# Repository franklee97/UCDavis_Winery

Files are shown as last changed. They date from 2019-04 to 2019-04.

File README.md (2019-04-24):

# UCDavis_Winery

This repo contains all the information regarding my project at UC Davis RMI Winery. The goal of the project was to come up with a system that can collect and record data from a fermentation tank inside the winery. The data that were collected were Brix, or sugar concentration of a wine, Redox, and temperature. This system consisted of a PCB carrier board with mounting holes and necessary electrical connections, modules that either plugged into the mounting holes of the carrier board or resided on a din rail, and a box to hold all the components and wires. This repo has software information as well as hardware and layout information of the box. The system was only tested with one fermentation tank, but it is capable of expanding the number of tanks by a simple change in code. It also has the capability of sending data wirelessly via Bluetooth or XBee.

## BOM
This folder has the Bill of Materials(BOM) necessary for this project. The parts were ordered in four different batches. `Final.xlsx` contains all the components that are necessary for this project as some parts were never used from other orders.

## Code
This folder contains the code necessary to collect data. It contains two Arduino code, `data_collection_brix.ino` and `data_collection_redox.ino`. They both use `ModbusMaster.h` library to read values from the slave devices and store into SD cards, but the brix code reads two sensors' data while the redox code read one sensor's data. The polling rates for each code are also different. The code was written for Arduino Mega board, but any Arduino boards with at least two Serial ports will suffice. 

### Data Format
The data are stored as `.csv` file. The sample data for each code are inside each code folder. The name of the file uses the following format: `DATA[month][date].csv`. For example, if it is a data file from January 5th, the filename would be `DATA15.csv`. A new file was created every day to prevent an overload inside one file. More information about how this was done is in the comments for each code.

## Diagram
This folder contains two files, `Circuit_Diagram.png` and `Data_Flow_2.0.pdf`. `Circuit_Diagram.png` shows a circuit level diagram of how everything is being powered. It also shows data communication as well. `Data_Flow_2.0.pdf` is a diagram that specifically shows how data is being transferred between the modules inside the system. `Circuit_Diagram.png` was created using EAGLE and `Data_Flow_2.0.pdf` was created using Microsoft Vizio.

## Schematic
This folder contains a folder named `carrier_final` which has the necessary EAGLE files for the carrier PCB. It also has a top and bottom layout pictures given by Oshpark. The folder contains `Archives` folder that has previous EAGLE designs.

## Solidworks
This folder has `.SLDPRT` files that was necessary for the design of the box. Some components were downloaded from the manufacturing websites, and some were created by me. `Final.SLDPRT` has all the components.

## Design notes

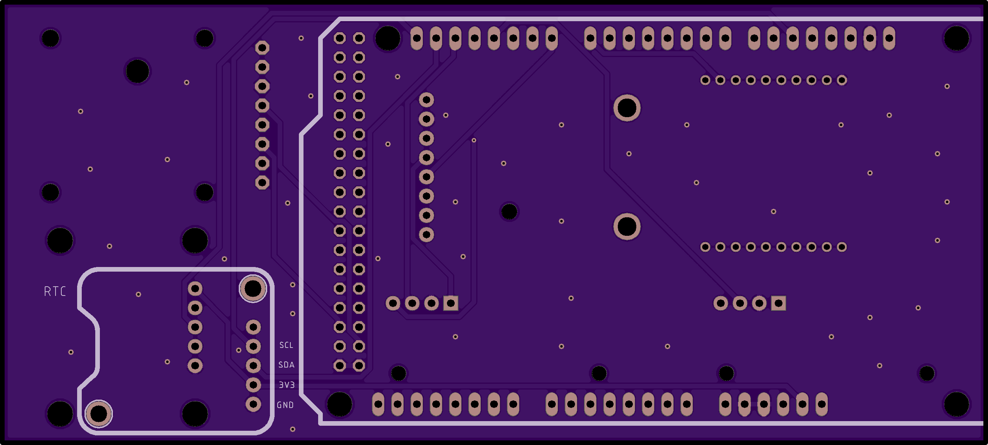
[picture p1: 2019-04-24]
Schematic/carrier_final/Bottom.png

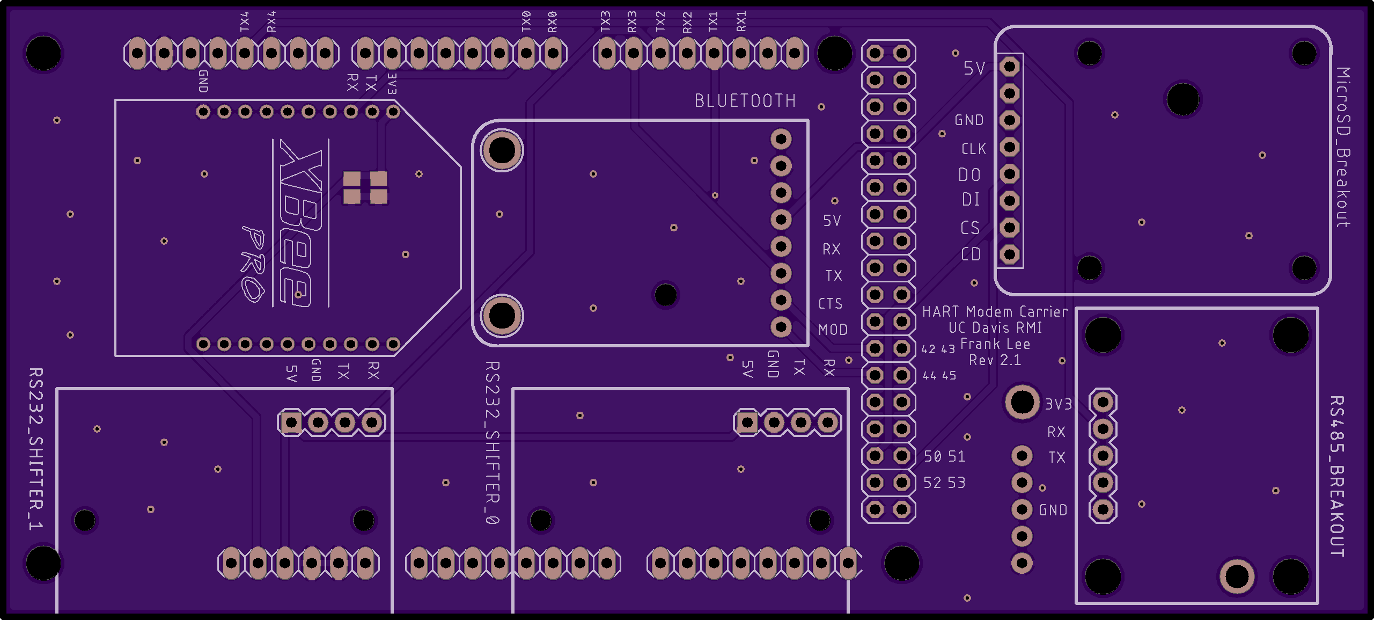
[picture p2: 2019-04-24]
Schematic/carrier_final/Top.png

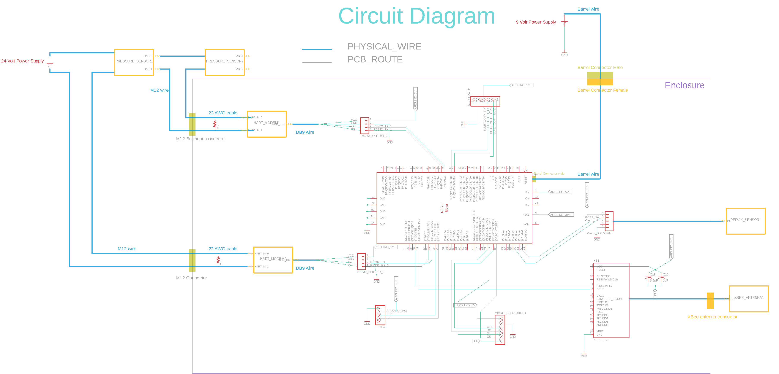
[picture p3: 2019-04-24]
Diagram/Circuit Diagram.png

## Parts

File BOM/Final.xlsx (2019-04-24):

Name | Description | Link | Price | Quantity |  | Arrived?
Modules
Arduino MEGA | Microcontroller with ability for module extension | https://store.arduino.cc/usa/arduino-mega-2560-rev3 | $38.50 | 2 | $77.00 | yes
RS232 Shifter without DB9 | RS232 shifter board | https://www.sparkfun.com/products/8780 | $9.95 | 2 | $19.90 | yes
MicroSD card breakout board | Allows MicroSD card to be inserted in Arduino | https://www.adafruit.com/product/254 | $7.50 | 1 | $7.50 | yes
250Ω Resistor | Resistor to put in current loop | link (https://www.procomsol.com/online_store/r_loop_250_ohm_hart_loop_resistor) | $5 | 3 | $15.00 | yes
HART Modem | Modem to convert HART to Modbus | link (https://microflx.com/products/microlink-hm-hart-protocol-modem-modbus-accumulator-rs-232-interface?variant=33428219782) | $225 | 2 | $450.00 | only one
Xbee module |  | https://www.digikey.com/product-detail/en/XBP24-AUI-001/XBP24-AUI-001-ND/935970 | $32.00 | 1 | $32.00
USB to RS232 | Cable required to configure the HART modem from computer | https://www.adafruit.com/product/18 | $14.95 | 1 | $14.95 | yes
Power supply for Arduino | 9V 1.5A AC/DC power supply for Arduino | https://www.sparkfun.com/products/298 | $5.95 | 1 | $5.95 | yes
Bluetooth module |  | https://www.adafruit.com/product/2479 | $17.5 | 1 | $17.50 | yes
External antenna for XBee |  | https://www.digikey.com/product-detail/en/W1038/553-1476-ND/1619691 | $6.86 | 1 | $6.86 | yes
DB9 Gender changer | M/M DB9 gender changer | https://www.digikey.com/product-detail/en/assmann-wsw-components/AB410/AE10295-ND/1630255 | $3.01 | 3 | $9.03 | yes
Xbee antenna wire |  | https://www.digikey.com/products/en/rf-if-and-rfid/rf-accessories/866?k=rp-sma%20to%20ufl | $5.15 | 1 | $5.15
RTC | Real Time Clock module to keep time | https://www.adafruit.com/product/3295 | $4.95 | 1 | $4.95 | yes
USB to RS485 | Useful to read Redox data from computer | https://www.amazon.com/gp/product/B00NKAJGZM/ref=ppx_yo_dt_b_asin_title_o09_s00?ie=UTF8&psc=1 | $6.99 | 1 | $6.99
RS485 to TTL | RS485 shifter for Redox | https://www.amazon.com/gp/product/B01FDD52Y2/ref=ppx_yo_dt_b_asin_title_o07_s00?ie=UTF8&psc=1 | $7.19 | 1 | $7.19
 |  |  |  |  |  |  | Total
Header pins |  |  |  |  |  |  | $1026.20
Xbee headers | header pins fo Xbee module | https://www.digikey.com/product-detail/en/NPPN101BFCN-RC/S5751-10-ND/804812 | $0.98 | 4 | $3.92 | yes
Mega headers | 2x18 | https://www.digikey.com/products/en?KeyWords=PPTC182LFBN-RC&WT.z_header=search_go | $2.06 | 2 | $4.12 | yes
 | 1x8 | https://www.digikey.com/products/en?KeyWords=PPTC081LFBN-RC&WT.z_header=search_go | $0.65 | 6 | $3.90 | yes
 | 1x6 | https://www.digikey.com/products/en?KeyWords=PPTC061LFBN-RC&WT.z_header=search_go | $0.52 | 2 | $1.04 | yes
module headers | 1x4 | https://www.digikey.com/product-detail/en/sullins-connector-solutions/PPTC041LFBN-RC/S7002-ND/810144 | $0.45 | 4 | $1.80 | yes
 | 1x8 | https://www.digikey.com/products/en?KeyWords=PPTC081LFBN-RC&WT.z_header=search_go | $0.65 | 2 | $1.30 | yes
 | 1x5 | https://www.digikey.com/product-detail/en/sullins-connector-solutions/PPTC051LFBN-RC/S6103-ND/807239 | $0.47 | 2 | $0.94 | yes
Module standoff | For RTC, MicroSD, Bluetooth modules | https://www.digikey.com/product-detail/en/raf-electronic-hardware/4504-256-AL-7/1772-1559-ND/7680970 | $1.00 | 10 | $10.00 | yes
 | For RS232 shifters | https://www.digikey.com/product-detail/en/wurth-electronics-inc/971100244/732-12918-ND/9488622 | $0.60 | 6 | $3.60 | yes
 | For RS485 shifter | https://www.digikey.com/product-detail/en/raf-electronic-hardware/4504-440-AL-7/1772-1889-ND/7681300 | $0.48 | 6 | $2.88 | yes
Breakaway header pins | To mount arduino on carrier | https://www.sparkfun.com/products/116 | $1.50 | 2 | $3.00 | yes
Misc
Fabrication | Fabrication for PCB |  | $100.00 | 1 | $100.00 | no
3/8 inch standoff (10pcs) | To mount Arduino onto mounting panel | https://www.sparkfun.com/products/10463 | $3.95 | 1 | $3.95 | yes
1/4 inch screws (10pcs) | For standoffs | https://www.sparkfun.com/products/10453 | $1.50 | 1 | $1.50 | yes
Standoff | Standoff for the PCB | https://www.digikey.com/product-detail/en/8407/8407K-ND/255374 | $1.19 | 4 | $4.76 | yes
Enclosure (10.00 x 7.00 x 4.06 inch) | New enclosure | https://www.polycase.com/ml-70f-1508 | $44.53 | 1 | $44.53
Mounting Panel | New mounting panel | https://www.polycase.com/ml-70k | $13.37 | 1 | $13.37
Din rail (35mm x 7.5mm x 225mm) | To mount HART modems | https://www.polycase.com/dr-56 | $7.71 | 1 | $7.71
9 Pin D Sub connector (Male) | 9 pin connector for RS232 between HART modem and shifter | https://www.digikey.com/product-detail/en/assmann-wsw-components/A-DS-09-LL-Z/AE10972-ND/1241781 | $0.51 | 2 | $1.02 | yes
9 Pin D Sub connector (Female) |  | https://www.digikey.com/product-detail/en/assmann-wsw-components/A-DF-09-LL-Z/AE11063-ND/5051922 | $0.54 | 2 | $1.08 | yes
Female DB9 | Female DB9, solderable | https://www.sparkfun.com/products/429 | $1.5 | 2 | $3.00 | yes
Power connector (Female) | Power connector for the Arduino | https://www.mouser.com/ProductDetail/Switchcraft/L712AS | $5.1 | 1 | $5.10 | yes
Power connector (Male) |  | https://www.mouser.com/ProductDetail/Switchcraft/S761KS17 | $5.43 | 1 | $5.43 | yes
Hook-up wire (Red) | 24 gauge single conductor cable | https://www.digikey.com/product-detail/en/cnc-tech/1569-24-1-0500-004-1-TS/CN521R-25-ND/7065819 | $5.62 | 1 | $5.62 | yes
Hook-up wire (White) |  | https://www.digikey.com/product-detail/en/cnc-tech/1569-24-1-0500-002-1-TS/CN519W-25-ND/7065817 | $5.62 | 1 | $5.62 | yes
Hook-up wire (Black) |  | https://www.digikey.com/product-detail/en/cnc-tech/1569-24-1-0500-001-1-TS/CN518B-25-ND/7065816 | $5.62 | 1 | $5.62 | yes
9 Pin Serial Ribbon Cable (18 inches) | Ribbon cable for RS232 between HART modem and shifter (may be too long) | https://www.smarthome.com/elk-w040a-m1-cable-to-db9-serial-ribbon-cable.html | $8.57 | 2 | $17.14 | yes
Connector + cable for Pressure sensor | M12 type connector and bare wire for pressure sensors | https://www.automationdirect.com/adc/Shopping/Catalog/Wiring_Solutions/Micro_(M12)_Receptacles/7231-13501-9710050 | $7.5 | 2 | $15.00 | yes
Power connector for sensor | 4 pin circular power connector for sensor current loop | https://www.digikey.com/product-detail/en/te-connectivity-amp-connectors/T4032014041-000/A126819-ND/7927418 | $5.63 | 1 | $5.63 | yes
Power connector cable for sensor | 4 pin circular power connector sensor | https://www.digikey.com/product-detail/en/omron-electronics-inc-emc-div/XS3F-M421-405-A/OR1156-ND/1829630 | $21.65 | 1 | $21.65 | yes
T-coupler M12 | Parallel combination of sensors | https://www.automationdirect.com/adc/Shopping/Catalog/Cables/Sensors_-z-_Switches/Field_Wireable_Connectors_-a-_T-Couplers/7000-41181-0000000 | $13.00 | 1 | $13.00 | yes | $1026.20
M12 female connector with wire | T-couple accepts female output | https://www.automationdirect.com/adc/Shopping/Catalog/Cables/Sensors_-z-_Switches/Micro_(M12)_Receptacles/7231-13541-9710050 | $7.50 | 2 | $15.00 | yes
M12 Male Connector | To house bare wires | https://www.automationdirect.com/adc/Shopping/Catalog/Wiring_Solutions/Field_Wireable_Connectors_-a-_T-Couplers/7000-12701-0000000 | $7.00 | 2 | $14.00 | yes
 |  |  |  |  | $0.00
 |  |  |  |  | $0.00
 |  |  |  |  | $0.00
 |  |  |  |  | $0.00
 |  |  |  |  | $0.00
 |  |  |  |  | $0.00

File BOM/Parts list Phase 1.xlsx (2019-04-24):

Name | Description | Link | Price | Quantity |  | Arrived?
Arduino MEGA | Microcontroller with ability for module extension | https://store.arduino.cc/usa/arduino-mega-2560-rev3 | $38.50 | 2 | $77.00 | yes
RS232 Shifter without DB9 | RS232 shifter board | https://www.sparkfun.com/products/8780 | $9.95 | 2 | $19.90 | yes
Male DB9 | Male DB9, solderable | https://www.jameco.com/z/1011-9P-R-9-Pin-D-Subminiature-Connector-Right-Angle-PC-Mount_104970.html | $1.09 | 2 | $2.18 | yes
Jumper Wire (M/M) (40pc) | 6'' jumper wire for communication | https://www.adafruit.com/product/758 | $4 | 1 | $4.00 | yes
HART Modem | Modem to convert HART to Modbus | link (https://microflx.com/products/microlink-hm-hart-protocol-modem-modbus-accumulator-rs-232-interface?variant=33428219782) | $225 | 2 | $450.00 | only one
250Ω Resistor | Resistor to put in current loop | link (https://www.procomsol.com/online_store/r_loop_250_ohm_hart_loop_resistor) | $5 | 3 | $15.00 | yes
Power supply for Arduino | 9V 1.5A AC/DC power supply for Arduino | https://www.sparkfun.com/products/298 | $5.95 | 1 | $5.95 | yes
USB to RS232 | Cable required to configure the HART modem from computer | https://www.adafruit.com/product/18 | $14.95 | 1 | $14.95 | yes
Bluetooth module |  |  |  |  |  | Total
 |  |  |  |  |  | $588.98

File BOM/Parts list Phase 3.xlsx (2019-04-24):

Name | Reason | Link | Price | Quantity |  | Arrived?
RS232 Shifter | Shorted one accidentally | https://www.sparkfun.com/products/8780 | $9.95 | 2 | $19.90
 |  |  |  |  | $0.00
module headers(1x4, 1x8, 1x5) | Need new PCB | https://www.digikey.com/product-detail/en/sullins-connector-solutions/PPTC041LFBN-RC/S7002-ND/810144 | $0.45 | 10 | $4.50
 |  | https://www.digikey.com/products/en?KeyWords=PPTC081LFBN-RC&WT.z_header=search_go | $0.65 | 10 | $6.50
 |  | https://www.digikey.com/product-detail/en/sullins-connector-solutions/PPTC051LFBN-RC/S6103-ND/807239 | $0.47 | 10 | $4.70
 |  |  |  |  | $0.00
PCB | Mistakes on positioning |  | $65.00 | 1 | $65.00
 |  |  |  |  | $0.00 |  | Total
DB9 Gender changer | HART modem and RS232 shifter both have female DB9 port | https://www.digikey.com/product-detail/en/norcomp-inc/GCLP09M09F/GCLP09M09F-ND/1754448 | $4.40 | 3 | $13.20 |  | $150.95
 |  |  |  |  | $0.00
Xbee module | Bought the wrong version | https://www.digikey.com/product-detail/en/XBP24-AUI-001/XBP24-AUI-001-ND/935970 | $32.00 | 1 | $32.00
Xbee antenna wire | Never bought it | https://www.digikey.com/products/en/rf-if-and-rfid/rf-accessories/866?k=rp-sma%20to%20ufl | $5.15 | 1 | $5.15
 |  |  |  |  | $0.00
 |  |  |  |  | $0.00
 |  |  |  |  | $0.00
 |  |  |  |  | $0.00
 |  |  |  |  | $0.00
 |  |  |  |  | $0.00
 |  |  |  |  | $0.00
 |  |  |  |  | $0.00
 |  |  |  |  | $0.00
 |  |  |  |  | $0.00
 |  |  |  |  | $0.00
 |  |  |  |  | $0.00
 |  |  |  |  | $0.00
 |  |  |  |  | $0.00
 |  |  |  |  | $0.00
 |  |  |  |  | $0.00
 |  |  |  |  | $0.00
 |  |  |  |  | $0.00
 |  |  |  |  | $0.00
 |  |  |  |  | $0.00
 |  |  |  |  | $0.00
 |  |  |  |  | $0.00
 |  |  |  |  | $0.00
 |  |  |  |  | $0.00
 |  |  |  |  | $0.00
 |  |  |  |  | $0.00
 |  |  |  |  | $0.00
 |  |  |  |  | $0.00
 |  |  |  |  | $0.00
 |  |  |  |  | $0.00
 |  |  |  |  | $0.00
 |  |  |  |  | $0.00
 |  |  |  |  | $0.00
 |  |  |  |  | $0.00

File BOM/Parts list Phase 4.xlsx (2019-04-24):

Name | Reason | Link | Price | Quantity |  | Arrived?
DB9 Female Serial Connector | Only have 2, might need extra | https://www.sparkfun.com/products/429 | $1.75 | 2 | $3.50 | yes
3/8 inch standoff (10pcs) | To mount Arduino onto mounting panel | https://www.sparkfun.com/products/10463 | $3.95 | 1 | $3.95 | yes
1/4 inch screws (10pcs) | For standoffs | https://www.sparkfun.com/products/10453 | $1.50 | 1 | $1.50 | yes
Enclosure (10.00 x 7.00 x 4.06 inch) | New enclosure | https://www.polycase.com/ml-70f-1508 | $44.53 | 1 | $44.53
Mounting Panel | New mounting panel | https://www.polycase.com/ml-70k | $13.37 | 1 | $13.37
Din rail (35mm x 7.5mm x 225mm) | To mount HART modems | https://www.polycase.com/dr-56 | $7.71 | 1 | $7.71
Breakaway header pins | To mount arduino on carrier | https://www.sparkfun.com/products/116 | $1.50 | 2 | $3.00 | yes
RS485 Shifter | One I have is faulty | https://www.sparkfun.com/products/10124 | $9.95 | 2 | $19.90 | yes
DB9 Gender changer | I accidentally bought M/F | https://www.digikey.com/product-detail/en/assmann-wsw-components/AB410/AE10295-ND/1630255 | $3.01 | 3 | $9.03 | yes
Screw terminals | For RS485 | https://www.sparkfun.com/products/8235 | $0.95 | 2 | $1.90 | yes | Total
T-coupler M12 | Parallel combination of sensors | https://www.automationdirect.com/adc/Shopping/Catalog/Cables/Sensors_-z-_Switches/Field_Wireable_Connectors_-a-_T-Couplers/7000-41181-0000000 | $13.00 | 1 | $13.00 | yes | $166.87
M12 female connector with wire | T-couple accepts female output | https://www.automationdirect.com/adc/Shopping/Catalog/Cables/Sensors_-z-_Switches/Micro_(M12)_Receptacles/7231-13541-9710050 | $7.50 | 2 | $15.00 | yes
M12 Male Connector | To house bare wires | https://www.automationdirect.com/adc/Shopping/Catalog/Wiring_Solutions/Field_Wireable_Connectors_-a-_T-Couplers/7000-12701-0000000 | $7.00 | 2 | $14.00 | yes
Module standoff | For RTC, MicroSD, Bluetooth modules | https://www.digikey.com/product-detail/en/raf-electronic-hardware/4504-256-AL-7/1772-1559-ND/7680970 | $1.00 | 10 | $10.00 | yes
 | For RS232 shifters | https://www.digikey.com/product-detail/en/wurth-electronics-inc/971100244/732-12918-ND/9488622 | $0.60 | 6 | $3.60 | yes
 | For RS485 shifter | https://www.digikey.com/product-detail/en/raf-electronic-hardware/4504-440-AL-7/1772-1889-ND/7681300 | $0.48 | 6 | $2.88 | yes
 |  |  |  |  | $0.00
 |  |  |  |  | $0.00
 |  |  |  |  | $0.00
 |  |  |  |  | $0.00
 |  |  |  |  | $0.00
 |  |  |  |  | $0.00
 |  |  |  |  | $0.00
 |  |  |  |  | $0.00
 |  |  |  |  | $0.00
 |  |  |  |  | $0.00
 |  |  |  |  | $0.00
 |  |  |  |  | $0.00
 |  |  |  |  | $0.00
 |  |  |  |  | $0.00
 |  |  |  |  | $0.00
 |  |  |  |  | $0.00
 |  |  |  |  | $0.00
 |  |  |  |  | $0.00
 |  |  |  |  | $0.00
 |  |  |  |  | $0.00
 |  |  |  |  | $0.00
 |  |  |  |  | $0.00
 |  |  |  |  | $0.00
 |  |  |  |  | $0.00
 |  |  |  |  | $0.00
 |  |  |  |  | $0.00
 |  |  |  |  | $0.00
 |  |  |  |  | $0.00
 |  |  |  |  | $0.00
 |  |  |  |  | $0.00
 |  |  |  |  | $0.00
 |  |  |  |  | $0.00

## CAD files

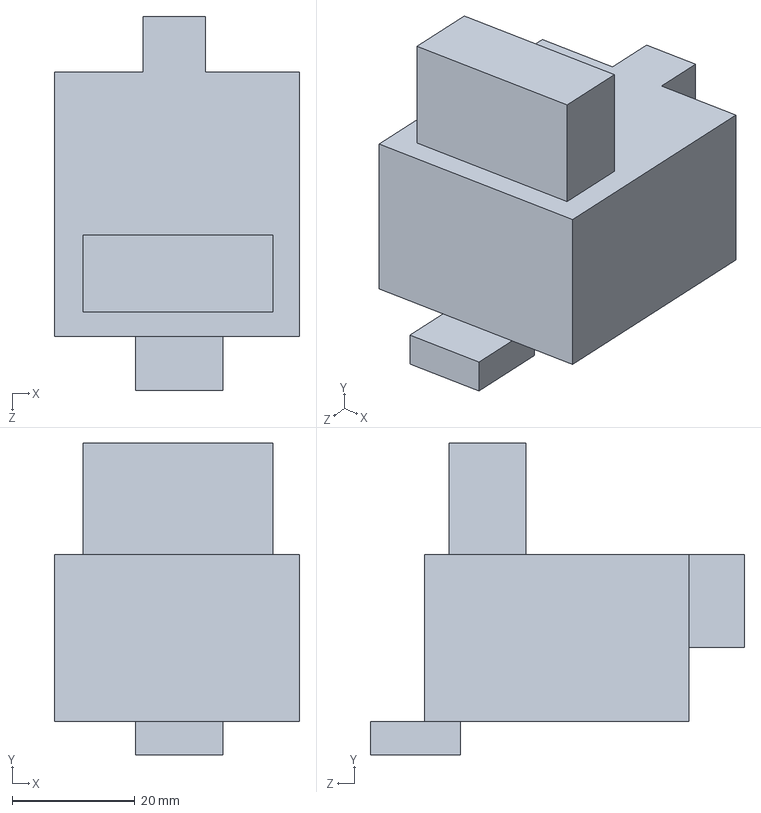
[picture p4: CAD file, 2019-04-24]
Solidworks/HART modem.SLDPRT
39.9 x 50.8 x 60.9 mm

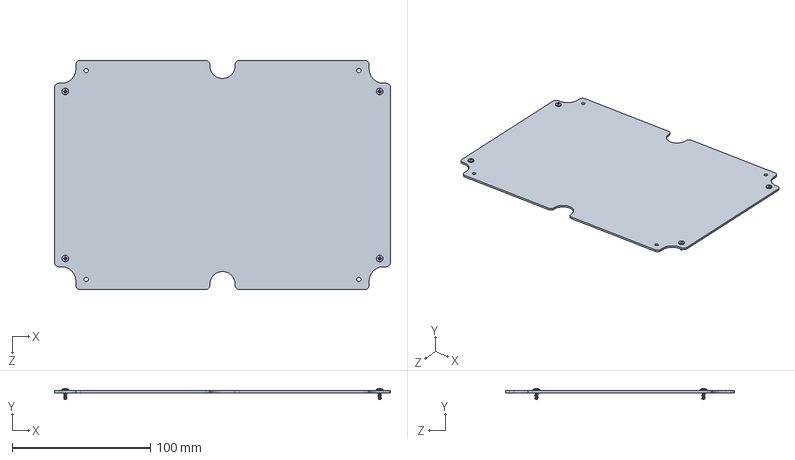
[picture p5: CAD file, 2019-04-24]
Solidworks/ML-70K.SLDPRT
242.6 x 7.99 x 165.6 mm

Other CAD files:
Solidworks/Sparkfun_RS232.SLDPRT

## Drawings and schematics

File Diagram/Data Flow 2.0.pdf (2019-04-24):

## Redox Sensor

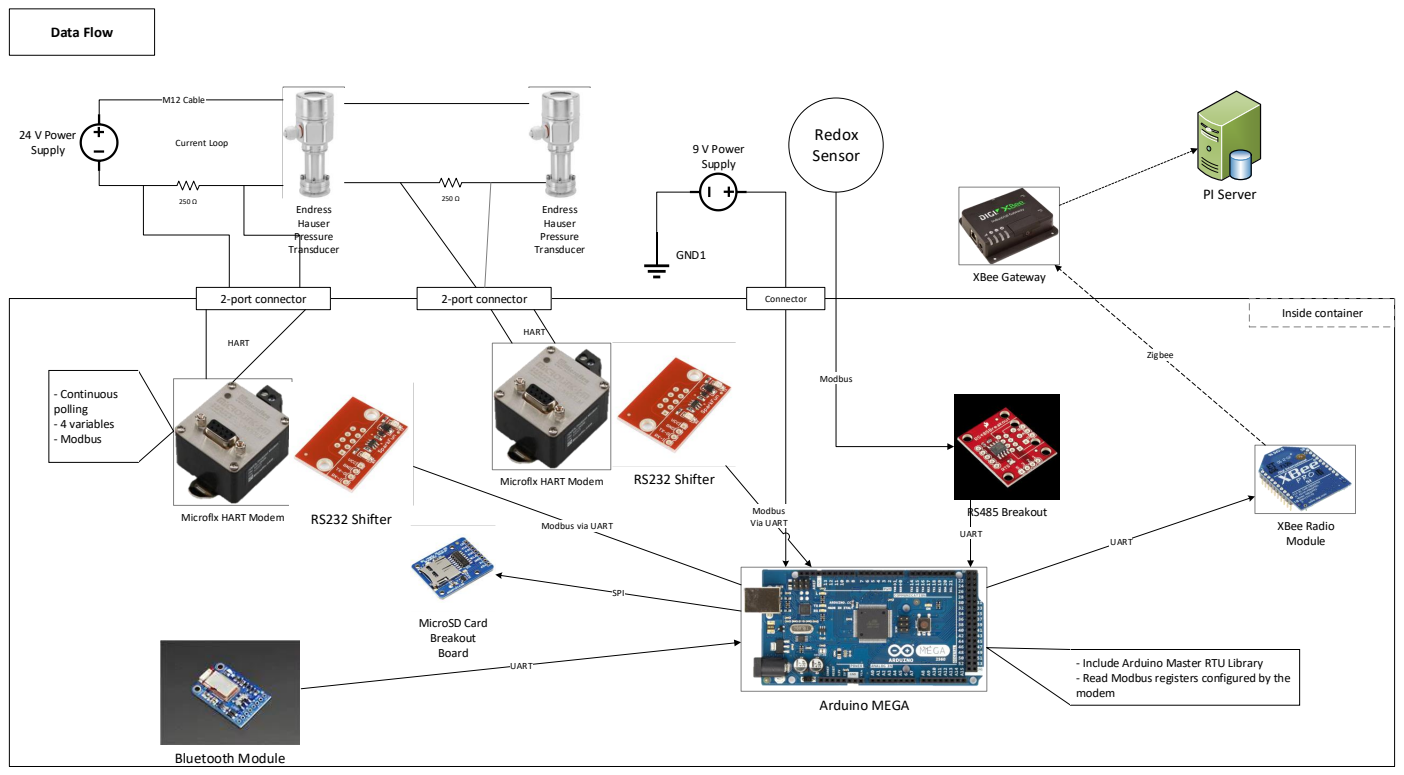
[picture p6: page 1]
24 V Power Supply; Endress Hauser Pressure Transducer; M12 Cable; Current Loop; HART; Arduino MEGA; MicroSD Card Breakout Board; SPI; UART; XBee Radio; Module; XBee Gateway; Zigbee; Inside container; PI Server; 2-port connector; 9 V Power Supply; GND1; Data Flow; Bluetooth Module; RS485 Breakout; Modbus; RS232 Shifter; Microflx HART Modem; Modbus Via UART; Connector; - Continuous polling - 4 variables - Modbus

Microflx HART Modem

Modbus via UART

- Include Arduino Master RTU Library
- Read Modbus registers configured by the
modem

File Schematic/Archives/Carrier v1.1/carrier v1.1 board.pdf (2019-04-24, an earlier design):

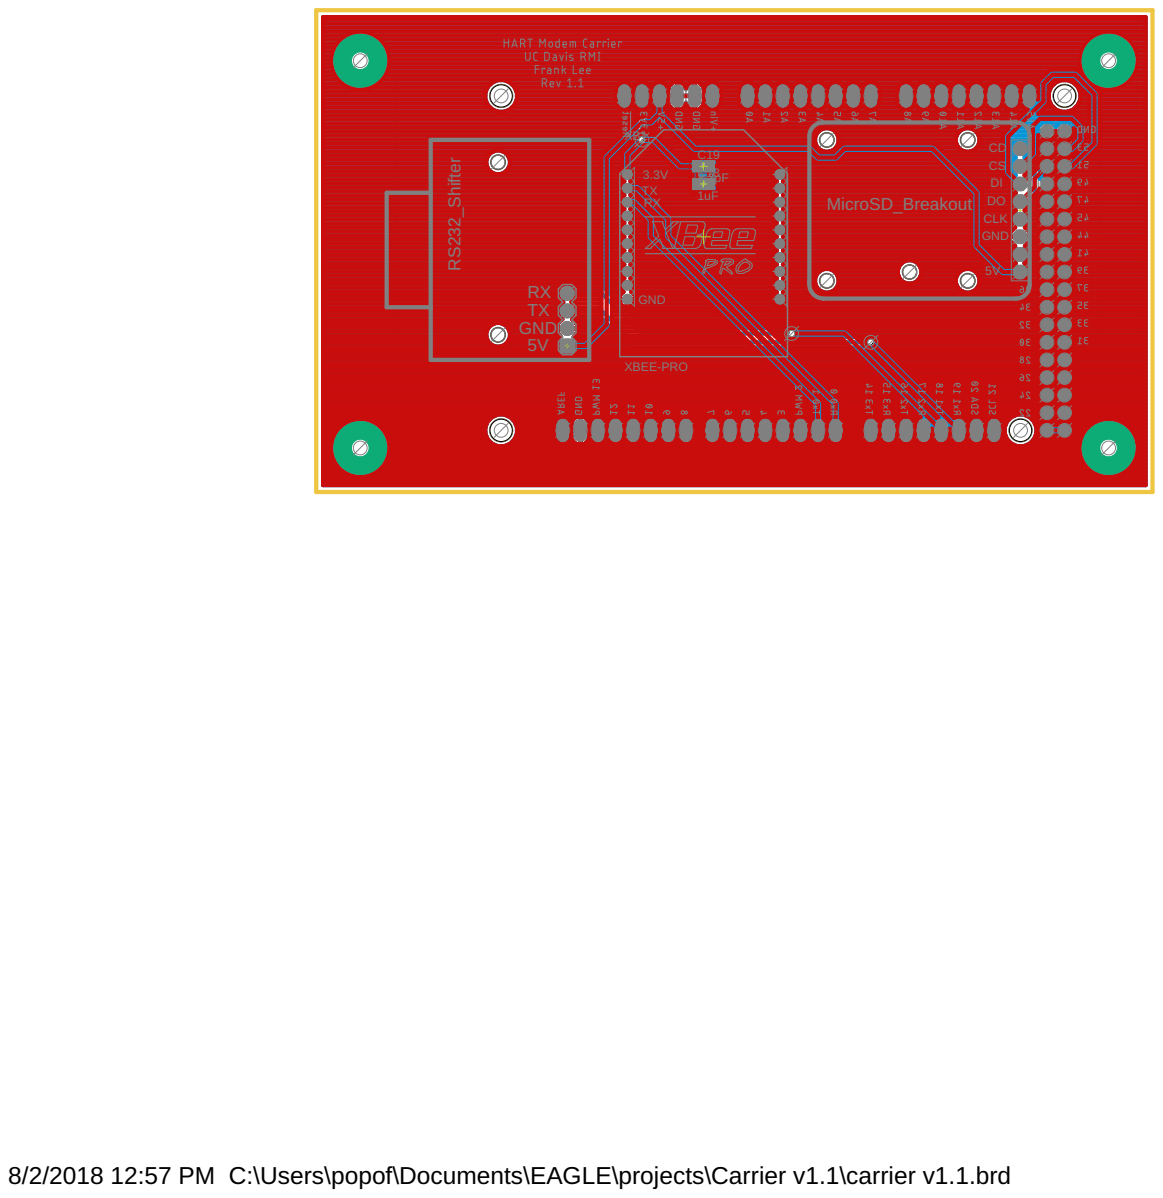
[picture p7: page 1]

8/2/2018 12:57 PM C:\Users\popof\Documents\EAGLE\projects\Carrier v1.1\carrier v1.1.brd

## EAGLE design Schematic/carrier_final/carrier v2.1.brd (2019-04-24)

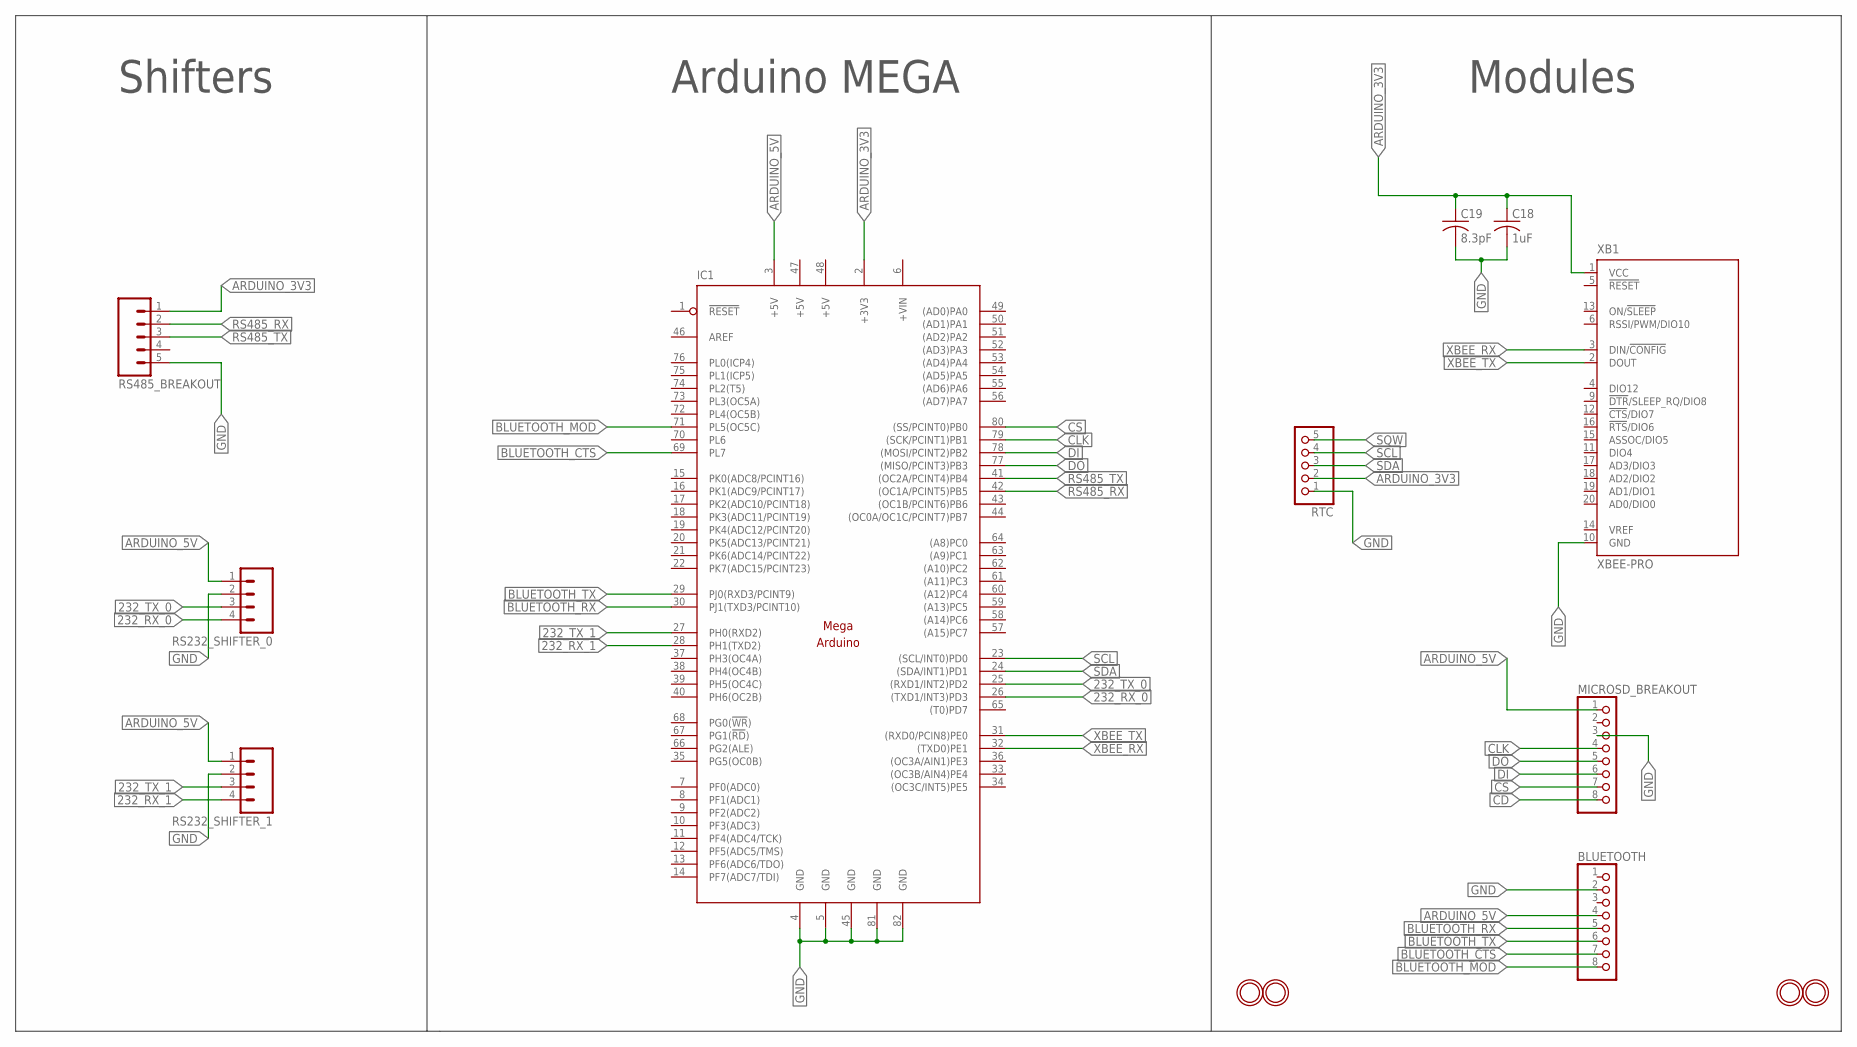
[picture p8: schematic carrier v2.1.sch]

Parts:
BLUETOOTH: HEADER-1X876MIL; 1X08_ROUND_76
C18: 1uF; C0805
C19: 8.3pF; C0805
IC1: MEGAARDUINO_1; MEGA_ARDUINO
MICROSD_BREAKOUT: PINHD-1X8BIG; 1X08-BIG
RS232_SHIFTER_0, RS232_SHIFTER_1: M04PTH; 1X04
RS485_BREAKOUT: M05PTH; 1X05
RTC: HEADER-1X576MIL; 1X05_ROUND_76
U$1, U$4: MOUNTINGHOLE2.0; MOUNTINGHOLE_2.0_PLATED
U$28, U$29: MOUNTINGHOLE2.5; MOUNTINGHOLE_2.5_PLATED
XB1: XBEE-PRO

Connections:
232_RX_0: IC1.26 ((TXD1/INT3)PD3), RS232_SHIFTER_0.4
232_RX_1: IC1.28 (PH1(TXD2)), RS232_SHIFTER_1.4
232_TX_0: IC1.25 ((RXD1/INT2)PD2), RS232_SHIFTER_0.3
232_TX_1: IC1.27 (PH0(RXD2)), RS232_SHIFTER_1.3
+5V: IC1.47 (+5V), IC1.48 (+5V)
+VIN: IC1.6 (+VIN)
ARDUINO_3V3: C18.1, C19.1, IC1.2 (+3V3), RS485_BREAKOUT.1, RTC.2, XB1.1 (VCC)
ARDUINO_5V: BLUETOOTH.4, IC1.3 (+5V), MICROSD_BREAKOUT.1, RS232_SHIFTER_0.1, RS232_SHIFTER_1.1
BLUETOOTH_CTS: BLUETOOTH.7, IC1.69 (PL7)
BLUETOOTH_MOD: BLUETOOTH.8, IC1.71 (PL5(OC5C))
BLUETOOTH_RX: BLUETOOTH.5, IC1.30 (PJ1(TXD3/PCINT10))
BLUETOOTH_TX: BLUETOOTH.6, IC1.29 (PJ0(RXD3/PCINT9))
CD: MICROSD_BREAKOUT.8
CLK: IC1.79 ((SCK/PCINT1)PB1), MICROSD_BREAKOUT.4
CS: IC1.80 ((SS/PCINT0)PB0), MICROSD_BREAKOUT.7
DI: IC1.78 ((MOSI/PCINT2)PB2), MICROSD_BREAKOUT.6
DO: IC1.77 ((MISO/PCINT3)PB3), MICROSD_BREAKOUT.5
GND: BLUETOOTH.2, C18.2, C19.2, IC1.4 (GND), IC1.5 (GND), IC1.45 (GND), IC1.81 (GND), IC1.82 (GND), MICROSD_BREAKOUT.3, RS232_SHIFTER_0.2, RS232_SHIFTER_1.2, RS485_BREAKOUT.5, RTC.1, XB1.10 (GND)
RS485_RX: IC1.42 ((OC1A/PCINT5)PB5), RS485_BREAKOUT.2
RS485_TX: IC1.41 ((OC2A/PCINT4)PB4), RS485_BREAKOUT.3
SCL: IC1.23 ((SCL/INT0)PD0), RTC.4
SDA: IC1.24 ((SDA/INT1)PD1), RTC.3
SQW: RTC.5
XBEE_RX: IC1.32 ((TXD0)PE1), XB1.3 (DIN/!CONFIG)
XBEE_TX: IC1.31 ((RXD0/PCIN8)PE0), XB1.2 (DOUT)

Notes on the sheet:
Shifters
Arduino MEGA
Modules

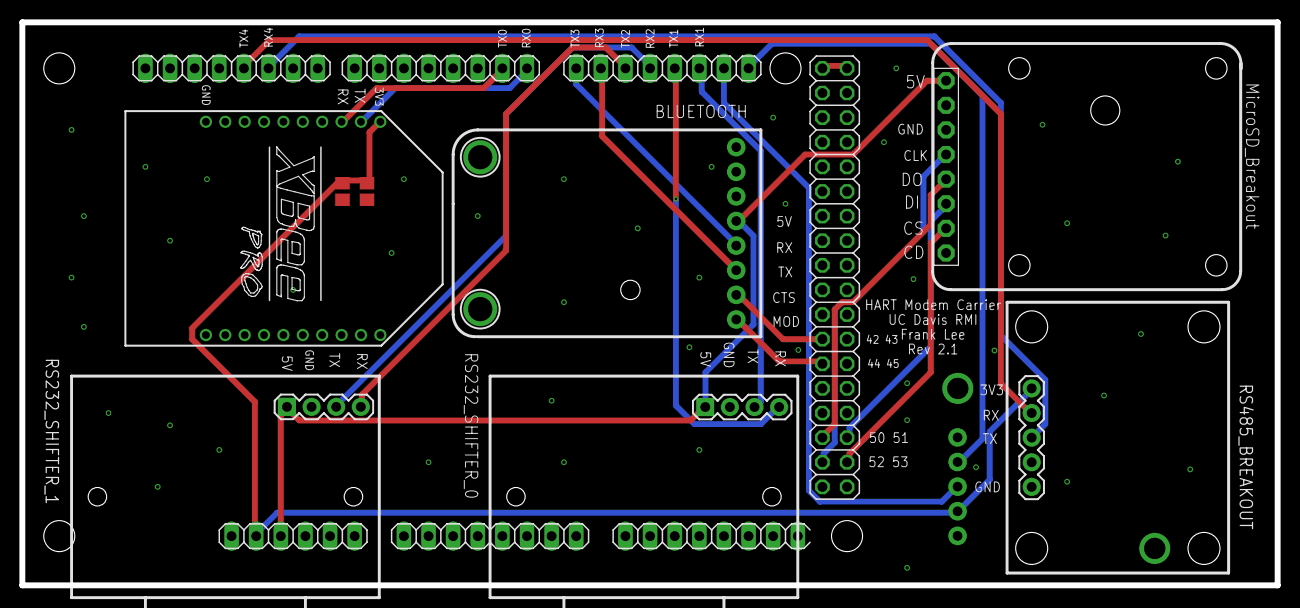
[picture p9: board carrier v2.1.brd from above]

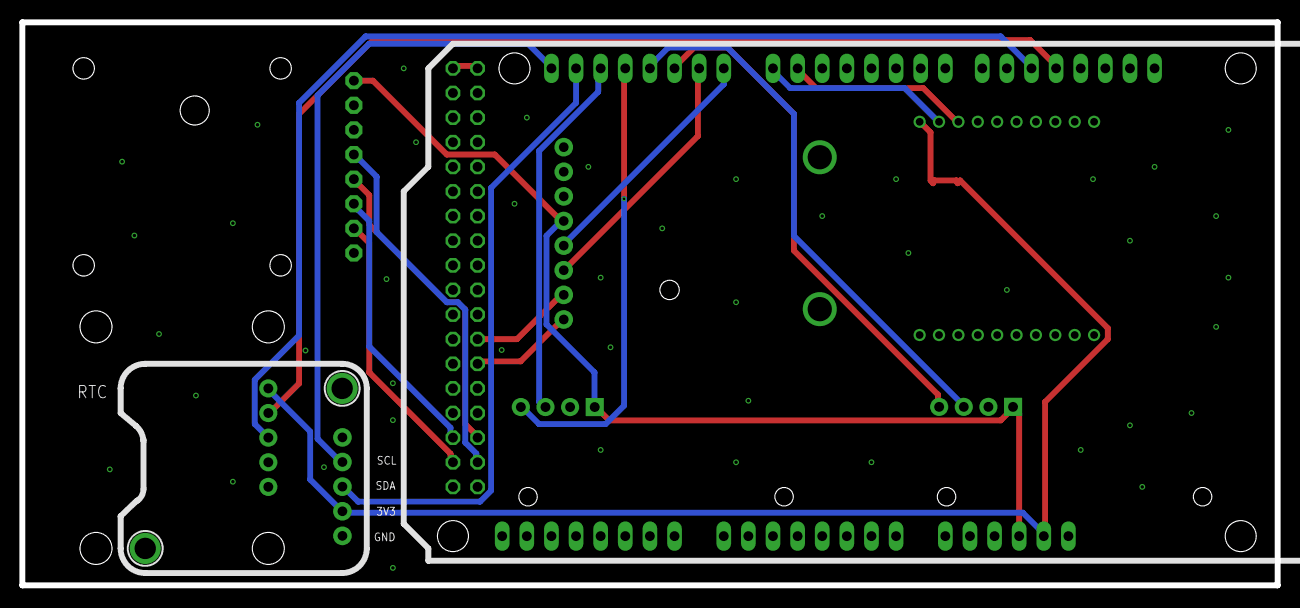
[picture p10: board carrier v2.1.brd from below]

Board: 2 copper layers, 129.5 x 58.1 mm, 18 parts (4 on the bottom side), 22 nets.

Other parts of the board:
JP6, JP7, JP8, JP15: STAND-OFF

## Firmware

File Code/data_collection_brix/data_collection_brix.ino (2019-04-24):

/*
   This code runs on Arduino Mega and collects data from two Brix sensor via one RS232
   using Modbus protocol. It then saves the data to a csv file. The polling rate
   can be changed.
   The following modules are necessary to run this code:
   RS 232 Shifter
   RTC chip
   SD Card module

*/

#include <RunningAverage.h>   // Necessary library to find running average of the values to prevent outliers
#include <SD.h>               // Library for SD card module functions
#include "RTClib.h"           // Access RTC functions
#include <Wire.h>             // Communicate with I2C devices
#include <ModbusMaster.h>     // Use for modbus protocol functions



// Instantiate
ModbusMaster node;            // Instantiate Modbus node
RTC_PCF8523 rtc;              // Instantiate rtc module
File myFile;                  // Instantiate File
RunningAverage sensor1RA(20); // Instantiate RunningAverage
RunningAverage sensor2RA(20);


// Initialize
String dataString = "";     // Initialize data string
String filename = "";       // Initialize filename
int samples = 0;            // Initialize sample

void setup()
{

  rtc.begin();        // Begin rtc module
  pinMode(53, OUTPUT);// Set pin 53 to OUTPUT for SD card communication
  SD.begin(53);       // Begin SD module
  // Clear any values in runningAverage
  sensor1RA.clear();
  sensor2RA.clear();


  // the DateTime class now is the current time given by rtc module
  DateTime now = rtc.now();

  Serial1.begin(9600);      // Modbus serial with baud rate 9600
  Serial.begin(4800);       // Serial for debugging
  delay(100);
  node.begin(1, Serial1);  // Modbus RTU
  delay(100);
  Serial.println("Connected ");
  Serial.println("Modbus RTU Master Online");

  // Define csv filename format
  filename = String("data") + String(now.month()) + String(now.day()) + String(".csv");

  // If the filename doesn't exist, create the header for CSV file. Header is the first row of CSV file
  if (!SD.exists(filename))
  {
    createHeader();
  }

}

/*
   Function to create the header of CSV file.
   It also updates the global filename value with current date
*/
void createHeader() {
  DateTime now = rtc.now();

  dataString = String("Timestamp") + "," + String("Sensor 1 Measured Pressure") + "," +  String("Sensor1 temp") + "," + String("Sensor 2 Measured Pressure") + "," + String("Sensor2 temp");

  filename = String("data") + String(now.month()) + String(now.day()) + String(".csv");
  saveData();
}


/*
   Necessary to convert float to decimal
*/
union ifloat
{
  uint8_t bytes[4];
  float val;
};

/*
   @param reg : the modbus register the user wishes to retrive data from
   This function reads the data on the modbus register as well as convert the value
   from float to decimal.
*/
float getData(int reg)
{

  node.readHoldingRegisters(reg, 2);

  signed long node1 = node.getResponseBuffer(0);
  word node2 = node.getResponseBuffer(1);

  byte msb3 = node1;
  byte msb4 = node1 >> 8;
  byte msb1 = node2;
  byte msb2 = node2 >> 8;
  ifloat f;
  f.bytes[3] = msb4;
  f.bytes[2] = msb3;
  f.bytes[1] = msb2;
  f.bytes[0] = msb1;

  node.clearResponseBuffer();

  return f.val;
}


void loop()
{

  DateTime now = rtc.now();
  // update global filename
  filename = String("data") + String(now.month()) + String(now.day()) + String(".csv");

  if (!SD.exists(filename))
  {
    createHeader();
  }


  int Mdelay = 3000;   // microdelay

  Serial.print("Sensor 1 Measured Pressure: "); // Debug
  float f_1_1 = getData(256);
  Serial.println(f_1_1, 20 );     // Debug

  Serial.print("Sensor1 temp: "); // Debug
  float f_1_temp = getData(262);
  Serial.println(f_1_temp, 20);   // Debug


  Serial.print("Sensor 2 Measured Pressure: "); // Debug
  float f_2_1 = getData(264);
  Serial.println(f_2_1, 20 );   // Debug

  Serial.print("Sensor2 temp: "); // Debug
  float f_2_temp = getData(270);
  Serial.println(f_2_temp, 20);   // Debug


  // Retrieve time data
  String y = String(now.year());
  String mo = String(now.month());
  String d = String(now.day());

  String h = String(now.hour());
  String m = String(now.minute());
  String s = String(now.second());

  // Debug
  Serial.print(h);
  Serial.print(m);
  Serial.print(s);
  Serial.println();


  // Concatenate time data
  String str = y + "/" + mo + "/" + d + " " + h + ":" + m + ":" + s;


  // Push to runningAverage
  sensor1RA.addValue(f_1_1);
  sensor2RA.addValue(f_2_1);
  Serial.println(samples);    // Debug



  samples++;
  if (samples == 20)      // Every minute, record the value given from runningAverage
  {
    samples = 0;

    dataString = str + "," + String(sensor1RA.getAverage(), 20) + "," + String(f_1_temp, 20) + "," + String(sensor2RA.getAverage(), 20) + "," + String(f_2_temp, 20);

    // Manually discard outliers
    if (sensor1RA.getAverage() < 2.5 && sensor2RA.getAverage() < 2.5) {
      saveData();
    }

    sensor1RA.clear();
    sensor2RA.clear();
    // Debug
    Serial.println(sensor1RA.getAverage(), 20);
    Serial.println(sensor2RA.getAverage(), 20);
  }


  delay(Mdelay);

  Serial.println();


}


/*
   This function opens the csv file and adds a row of data
*/
void saveData() {
  myFile = SD.open(filename, FILE_WRITE);

  if (SD.exists(filename))
  {
    if (myFile) {
      myFile.println(dataString);
      myFile.close(); // close the file
    }
  }
  else
  {
    Serial.println("Error writing to file !");
  }

}

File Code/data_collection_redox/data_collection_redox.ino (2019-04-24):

/*
   This code runs on Arduino Mega and collects data from a redox sensor via RS485
   using Modbus protocol. It then saves the data to a csv file. The polling rate
   can be changed.
   The following modules are necessary to run this code:
   RS485 to TTL
   RTC chip
   SD Card module

*/


#include <RunningAverage.h>   // Necessary library to find running average of the values to prevent outliers
#include <SD.h>               // Library for SD card module functions
#include "RTClib.h"           // Access RTC functions
#include <Wire.h>             // Communicate with I2C devices
#include <ModbusMaster.h>     // Use for modbus protocol functions


// Rx/Tx is hooked up to Serial1 and Data Enable, Receive Enable are hooked up as follows:
#define MAX485_DE   17
#define MAX485_RE_NEG   16


// Instantiate
RTC_PCF8523 rtc;            // Instantiate rtc module
File myFile;                // Instantiate File
RunningAverage redoxRA(20);       // Instantiate RunningAverage
RunningAverage temperatureRA(20);
ModbusMaster node;          // Instantiate Modbus node


// Initialize
String dataString = "";     // Initialize data string
String filename = "";       // Initialize filename
int samples = 0;            // Initialize sample


// Necessary enable functions before and after transmiaaion
void preTransmission()
{
  digitalWrite(MAX485_RE_NEG, 1);
  digitalWrite(MAX485_DE, 1);
}

void postTransmission()
{
  digitalWrite(MAX485_RE_NEG, 0);
  digitalWrite(MAX485_DE, 0);
}




void setup() {

  rtc.begin();        // Begin rtc module
  pinMode(53, OUTPUT);// Set pin 53 to OUTPUT for SD card communication
  SD.begin(53);       // Begin SD module
  redoxRA.clear();    // Clear any values in the RunningAverage
  temperatureRA.clear();


  DateTime now = rtc.now();     // the DateTime class now is the current time given by rtc module

  // Set pinmodes for enable lines
  pinMode(MAX485_RE_NEG, OUTPUT);
  pinMode(MAX485_DE, OUTPUT);


  // Manually write low to the enable lines
  digitalWrite(MAX485_RE_NEG, 0);
  digitalWrite(MAX485_DE, 0);


  delay(100);


  Serial1.begin(19200);       // Modbus serial with baud rate 19200
  node.begin(1, Serial1);     // Begin modbus in Serial1
  delay(100);
  Serial.begin(9600);         // Serial for debugging

  node.preTransmission(preTransmission);
  node.postTransmission(postTransmission);


  // Hello world
  Serial.println("Goodnight moon!");

  delay(100);


  // Define csv filename format
  filename = String("data") + String(now.month()) +
             String(now.day()) + String(".csv");



  // If the filename doesn't exist, create the header for CSV file. Header is the first row of CSV file
  if (!SD.exists(filename))
  {
    createHeader();
  }


}

/*
   Function to create the header of CSV file.
   It also updates the global filename value with current date
*/
void createHeader() {
  DateTime now = rtc.now();

  dataString = String("Timestamp") + "," + String("Redox value") +
               "," + String("Temperature");

  filename = String("data") + String(now.month()) +
             String(now.day()) + String(".csv");

  saveData();
}


/*
   Necessary to convert float to decimal
*/
union ifloat
{
  uint8_t bytes[4];
  float val;
};

/*
   @param reg : the modbus register the user wishes to retrive data from
   This function reads the data on the modbus register as well as convert the value
   from float to decimal.
*/
float getData(int reg)
{
  node.readHoldingRegisters(reg, 10);

  signed long node1 = node.getResponseBuffer(3);
  word node2 = node.getResponseBuffer(2);

  byte msb3 = node1;
  byte msb4 = node1 >> 8;
  byte msb1 = node2;
  byte msb2 = node2 >> 8;
  ifloat f;
  f.bytes[3] = msb4;
  f.bytes[2] = msb3;
  f.bytes[1] = msb2;
  f.bytes[0] = msb1;


  node.clearResponseBuffer();

  return f.val;
}

void loop() { // run over and over

  DateTime now = rtc.now();
  // update global filename
  filename = String("data") + String(now.month()) +
             String(now.day()) + String(".csv");


  // same as in setup()
  if (!SD.exists(filename))
  {
    createHeader();
  }

  int MDelay = 3000;

  // Debug
  Serial.print("Redox: ");
  float f_1 = getData(2089);
  Serial.println(f_1, 20);

  Serial.print("Temperature: ");
  float f_2 = getData(2409);
  Serial.println(f_2, 20);


  // Retrieve time data
  String y = String(now.year());
  String mo = String(now.month());
  String d = String(now.day());

  String h = String(now.hour());
  String m = String(now.minute());
  String s = String(now.second());


  // Debug
  Serial.print(h);
  Serial.print(m);
  Serial.print(s);
  Serial.println();


  // Concatenate time data
  String str = y + "/" + mo + "/" + d + " " + h + ":" + m + ":" + s;


  // Push to runningAverage
  redoxRA.addValue(f_1);
  temperatureRA.addValue(f_2);

  Serial.println(samples);      // debug
  samples++;

  if (samples == 300)     // Every 15 minutes, record the value given from runningAverage
  {
    samples = 0;
    dataString = str + "," + String(redoxRA.getAverage(), 20) +
                 "," + String(temperatureRA.getAverage(), 20);

    // Manually discard outliers
    if (redoxRA.getAverage() < 3000 && temperatureRA.getAverage() < 100) {
      saveData();
    }

    redoxRA.clear();
    temperatureRA.clear();

    // Debug
    Serial.println(redoxRA.getAverage(), 20);
    Serial.println(temperatureRA.getAverage(), 20);
  }

  delay(MDelay);
  Serial.println();

}


/*
   This function opens the csv file and adds a row of data
*/
void saveData() {

  myFile = SD.open(filename, FILE_WRITE);

  Serial.println(myFile);
  Serial.println(filename);

  if (SD.exists(filename))
  {
    if (myFile) {
      myFile.println(dataString);
      myFile.close(); // close the file
    }
  }
  else
  {
    Serial.println("Error writing to file !");
  }

}

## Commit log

2019-04-24 Added schematics
    [carrier v2.1.brd, carrier v2.1.sch]
2019-04-24 added solidworks, circuit diagram, and archived carrier designs
    [Circuit Diagram.brd, Circuit Diagram.sch, HART modem.SLDPRT, ML-70K.SLDPRT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]
2019-04-24 layer view of the final board
2019-04-24 Update circuit diagram
2019-04-24 Update data flow and circuit diagram
2019-04-24 Update BOM
    [Final.xlsx, Parts list Phase 1.xlsx, Parts list Phase 2.xlsx, Parts list Phase 3.xlsx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]
2019-04-24 Added sample data
    [DATA1026.CSV, DATA115.CSV]
2019-04-24 Added RS485 modules in BOM
    [Final.xlsx]

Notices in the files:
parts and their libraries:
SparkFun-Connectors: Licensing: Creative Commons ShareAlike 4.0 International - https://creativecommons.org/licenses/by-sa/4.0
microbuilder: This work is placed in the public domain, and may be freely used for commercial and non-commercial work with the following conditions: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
